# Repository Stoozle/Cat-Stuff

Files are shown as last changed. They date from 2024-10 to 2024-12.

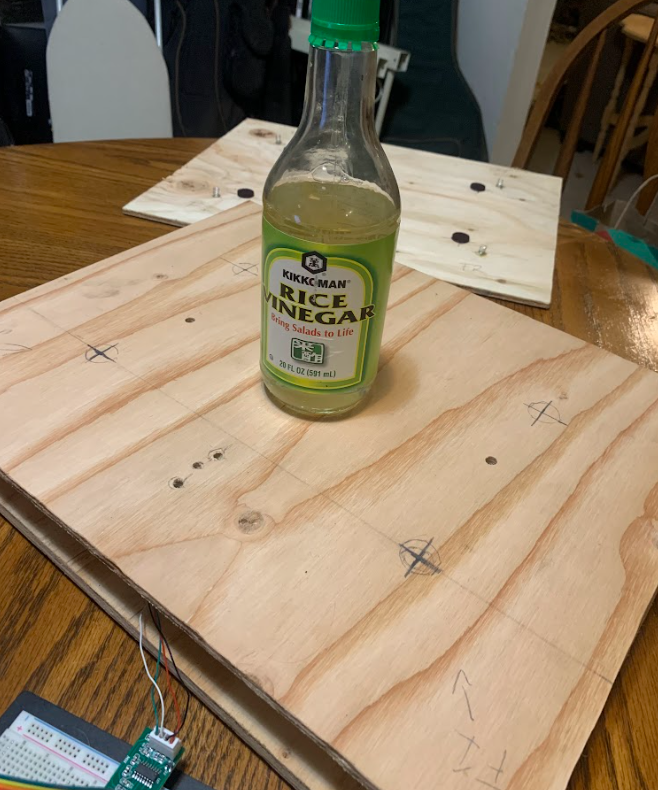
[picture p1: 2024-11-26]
testing/11_15_force_distrubution/center_board.png

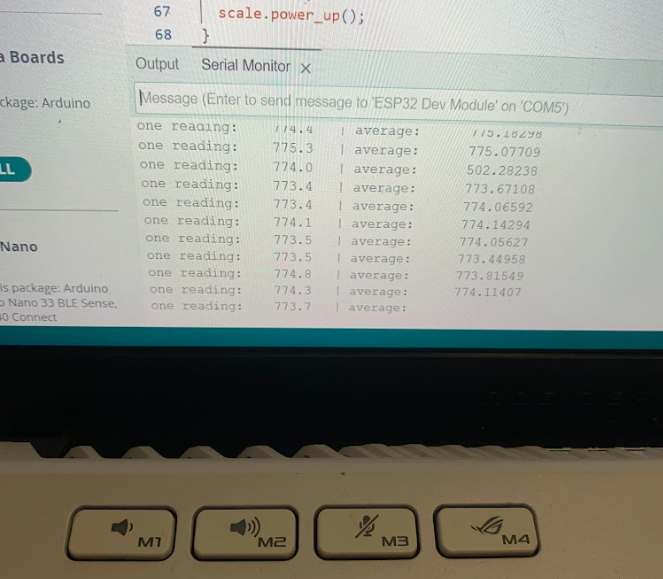
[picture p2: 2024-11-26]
testing/11_15_force_distrubution/left_output.png

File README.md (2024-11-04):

# FLOPS (FeLine Obesity Prevention System)
## High level description (project in development and much is subject to change and refinement)
* Cat owner's may want to monitor their cat's weight for various reasons. This project is intended to provide a system that will automatically measures a cat's weight. Measurement data can be used to inform appropriate modifications to a cat's diet in order to meet a target weight.
## Theory of operation
* Takes a cat's weight measurement every time it sleeps in its bed
* Allows user to observe plot of weight measurements over time

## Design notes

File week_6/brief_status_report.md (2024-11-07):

## Brief status report for team 09

So far we have
* Ordered inital parts/sensors
* Tested flexible force sensors (to detect weight in fixture) to observe output in a simple circuit
* Tested load cell with ADC and acquired weight measurement of a soda can that matches a kitchen scale
* Made progress with communicating with the ESP32 over WiFi
* Narrowed down options for methods of producing the outputs we need to make the scale work, and the types of components we'll need for the peripheral circuitry

We were feeling a little behind but are grinding to catch up and get ahead. The next glut of parts will be in the mail shortly, and more specific testing is soon to follow.

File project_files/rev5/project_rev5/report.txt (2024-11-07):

Info: Processing symbol 'C1:'.
Info: Processing symbol 'U3:'.
Info: Processing symbol 'C2:'.
Info: Processing symbol 'R7:'.
Info: Processing symbol 'C3:'.
Info: Processing symbol 'U1:Package_SO:SOP-16_3.9x9.9mm_P1.27mm'.
Info: Processing symbol 'C4:'.
Info: Processing symbol 'R8:'.
Info: Processing symbol 'J1:'.
Info: Processing symbol 'U2:RF_Module:ESP32-WROOM-32'.
Info: Processing symbol 'J2:'.
Info: Processing symbol 'R9:'.
Info: Processing symbol 'J3:'.
Info: Processing symbol 'X1:Oscillator:Oscillator_DIP-14'.
Info: Processing symbol 'J4:'.
Info: Processing symbol 'R1:'.
Info: Processing symbol 'J5:'.
Info: Processing symbol 'R10:'.
Info: Processing symbol 'J6:'.
Info: Processing symbol 'R2:'.
Info: Processing symbol 'Q1:'.
Info: Processing symbol 'U6:'.
Info: Processing symbol 'Q2:Package_TO_SOT_THT:TO-92_Inline'.
Info: Processing symbol 'R3:'.
Info: Processing symbol 'R11:'.
Info: Processing symbol 'R4:'.
Info: Processing symbol 'U4:'.
Info: Processing symbol 'R5:'.
Info: Processing symbol 'SW1:'.
Info: Processing symbol 'R6:'.
Connected U2 pin 39 to GND.
Connected U2 pin 1 to GND.
Connected U2 pin 39 to GND.
Add net unconnected-(U2-SCK/CLK-Pad20).
Connected U2 pin 20 to unconnected-(U2-SCK/CLK-Pad20).
Added X1 (footprint 'Oscillator:Oscillator_DIP-14').
Changed REF** reference designator to X1.
Changed X1 value from Oscillator_DIP-14 to ACO-11MHz.
Updated X1 symbol association from  to /a301af15-4480-4dae-a242-64f552d5c465.
Updated X1 fields.
Updated X1 sheetname to 'Root'.
Added Q2 (footprint 'Package_TO_SOT_THT:TO-92_Inline').
Changed REF** reference designator to Q2.
Changed Q2 value from TO-92_Inline to S8550.
Updated Q2 symbol association from  to /422a7e9a-33ed-4cef-8547-62cccaa18b52.
Updated Q2 fields.
Updated Q2 sheetname to 'Root'.
Updated Q2 sheetfile to 'project1.kicad_sch'.
Updated Q2 footprint filters to 'TO?92*'.
Add net +3.3V.
Connected Q2 pin 1 to +3.3V.
Add net Net-(Q2-B).
Connected Q2 pin 2 to Net-(Q2-B).
Add net Net-(J2-Pin_1).
Connected Q2 pin 3 to Net-(J2-Pin_1).
Updated X1 sheetfile to 'project1.kicad_sch'.
Updated X1 footprint filters to 'Oscillator*DIP*14*'.
Connected X1 pin 14 to +3.3V.
Connected X1 pin 7 to GND.
Add net unconnected-(X1-OUT-Pad8).
Connected X1 pin 8 to unconnected-(X1-OUT-Pad8).
Add net unconnected-(X1-NC-Pad1).
Connected X1 pin 1 to unconnected-(X1-NC-Pad1).
Added U1 (footprint 'Package_SO:SOP-16_3.9x9.9mm_P1.27mm').
Changed REF** reference designator to U1.
Changed U1 value from SOP-16_3.9x9.9mm_P1.27mm to HX711.
Updated U1 symbol association from  to /569d6c08-9232-4001-98fb-e43093d856b7.
Updated U1 fields.
Updated U1 sheetname to 'Root'.
Updated U1 sheetfile to 'project1.kicad_sch'.
Updated U1 footprint filters to 'SOP*3.9x9.9mm*P1.27mm*'.
Add net GND.
Connected U1 pin 5 to GND.
Connected U1 pin 14 to GND.
Add net unconnected-(U1-XO-Pad13).
Connected U1 pin 13 to unconnected-(U1-XO-Pad13).
Connected U1 pin 15 to GND.
Add net Net-(U1-VBG).
Connected U1 pin 6 to Net-(U1-VBG).
Connected U1 pin 10 to GND.
Connected U1 pin 1 to +3.3V.
Add net Net-(U1-INA-).
Connected U1 pin 7 to Net-(U1-INA-).
Connected U1 pin 9 to GND.
Add net Net-(U1-VFB).
Connected U1 pin 4 to Net-(U1-VFB).
Add net Net-(U1-PD_SCK).
Connected U1 pin 11 to Net-(U1-PD_SCK).
Connected U1 pin 3 to Net-(J2-Pin_1).
Connected U1 pin 16 to +3.3V.
Add net Net-(U1-DOUT).
Connected U1 pin 12 to Net-(U1-DOUT).
Add net Net-(U1-INA+).
Connected U1 pin 8 to Net-(U1-INA+).
Connected U1 pin 2 to Net-(Q2-B).
Added U2 (footprint 'RF_Module:ESP32-WROOM-32').
Changed REF** reference designator to U2.
Updated U2 symbol association from  to /1d41e7d4-28ae-44ed-bed4-c70fb3c3bb19.
Updated U2 fields.
Updated U2 sheetname to 'Root'.
Updated U2 sheetfile to 'project1.kicad_sch'.
Updated U2 footprint filters to 'ESP32?WROOM?32*'.
Add net unconnected-(U2-TXD0/IO1-Pad35).
Connected U2 pin 35 to unconnected-(U2-TXD0/IO1-Pad35).
Connected U2 pin 39 to GND.
Add net unconnected-(U2-EN-Pad3).
Connected U2 pin 3 to unconnected-(U2-EN-Pad3).
Add net unconnected-(U2-NC-Pad32).
Connected U2 pin 32 to unconnected-(U2-NC-Pad32).
Add net unconnected-(U2-IO2-Pad24).
Connected U2 pin 24 to unconnected-(U2-IO2-Pad24).
Add net Net-(Q1-D).
Connected U2 pin 7 to Net-(Q1-D).
Connected U2 pin 27 to Net-(U1-DOUT).
Add net unconnected-(U2-SENSOR_VP-Pad4).
Connected U2 pin 4 to unconnected-(U2-SENSOR_VP-Pad4).
Connected U2 pin 39 to GND.
Connected U2 pin 39 to GND.
Connected U2 pin 15 to GND.
Connected U2 pin 39 to GND.
Add net unconnected-(U2-IO19-Pad31).
Connected U2 pin 31 to unconnected-(U2-IO19-Pad31).
Add net unconnected-(U2-SCS/CMD-Pad19).
Connected U2 pin 19 to unconnected-(U2-SCS/CMD-Pad19).
Connected U2 pin 39 to GND.
Connected U2 pin 39 to GND.
Connected U2 pin 39 to GND.
Add net unconnected-(U2-IO23-Pad37).
Connected U2 pin 37 to unconnected-(U2-IO23-Pad37).
Add net unconnected-(U2-SENSOR_VN-Pad5).
Connected U2 pin 5 to unconnected-(U2-SENSOR_VN-Pad5).
Connected U2 pin 39 to GND.
Add net unconnected-(U2-SDI/SD1-Pad22).
Connected U2 pin 22 to unconnected-(U2-SDI/SD1-Pad22).
Connected U2 pin 39 to GND.
Connected U2 pin 39 to GND.
Connected U2 pin 39 to GND.
Add net unconnected-(U2-IO32-Pad8).
Connected U2 pin 8 to unconnected-(U2-IO32-Pad8).
Connected U2 pin 26 to Net-(U1-PD_SCK).
Add net unconnected-(U2-IO34-Pad6).
Connected U2 pin 6 to unconnected-(U2-IO34-Pad6).
Connected U2 pin 38 to GND.
Add net unconnected-(U2-RXD0/IO3-Pad34).
Connected U2 pin 34 to unconnected-(U2-RXD0/IO3-Pad34).
Connected U2 pin 39 to GND.
Connected U2 pin 39 to GND.
Add net unconnected-(U2-IO27-Pad12).
Connected U2 pin 12 to unconnected-(U2-IO27-Pad12).
Add net unconnected-(U2-SDO/SD0-Pad21).
Connected U2 pin 21 to unconnected-(U2-SDO/SD0-Pad21).
Add net unconnected-(U2-IO26-Pad11).
Connected U2 pin 11 to unconnected-(U2-IO26-Pad11).
Add net unconnected-(U2-IO14-Pad13).
Connected U2 pin 13 to unconnected-(U2-IO14-Pad13).
Add net unconnected-(U2-SHD/SD2-Pad17).
Connected U2 pin 17 to unconnected-(U2-SHD/SD2-Pad17).
Add net unconnected-(U2-IO12-Pad14).
Connected U2 pin 14 to unconnected-(U2-IO12-Pad14).
Connected U2 pin 39 to GND.
Add net unconnected-(U2-IO33-Pad9).
Connected U2 pin 9 to unconnected-(U2-IO33-Pad9).
Connected U2 pin 39 to GND.
Add net unconnected-(U2-IO18-Pad30).
Connected U2 pin 30 to unconnected-(U2-IO18-Pad30).
Add net unconnected-(U2-IO0-Pad25).
Connected U2 pin 25 to unconnected-(U2-IO0-Pad25).
Add net unconnected-(U2-IO15-Pad23).
Connected U2 pin 23 to unconnected-(U2-IO15-Pad23).
Connected U2 pin 39 to GND.
Add net unconnected-(U2-IO22-Pad36).
Connected U2 pin 36 to unconnected-(U2-IO22-Pad36).
Connected U2 pin 39 to GND.
Connected U2 pin 39 to GND.
Add net unconnected-(U2-IO25-Pad10).
Connected U2 pin 10 to unconnected-(U2-IO25-Pad10).
Add net unconnected-(U2-SWP/SD3-Pad18).
Connected U2 pin 18 to unconnected-(U2-SWP/SD3-Pad18).
Connected U2 pin 39 to GND.
Connected U2 pin 39 to GND.
Connected U2 pin 2 to +3.3V.
Add net unconnected-(U2-IO17-Pad28).
Connected U2 pin 28 to unconnected-(U2-IO17-Pad28).
Add net unconnected-(U2-IO21-Pad33).
Connected U2 pin 33 to unconnected-(U2-IO21-Pad33).
Add net unconnected-(U2-IO13-Pad16).
Connected U2 pin 16 to unconnected-(U2-IO13-Pad16).
Add net unconnected-(U2-IO5-Pad29).
Connected U2 pin 29 to unconnected-(U2-IO5-Pad29).
Error: Cannot add C1 (no footprint assigned).
Error: Cannot add C2 (no footprint assigned).
Error: Cannot add C3 (no footprint assigned).
Error: Cannot add C4 (no footprint assigned).
Error: Cannot add J1 (no footprint assigned).
Error: Cannot add J2 (no footprint assigned).
Error: Cannot add J3 (no footprint assigned).
Error: Cannot add J4 (no footprint assigned).
Error: Cannot add J5 (no footprint assigned).
Error: Cannot add J6 (no footprint assigned).
Error: Cannot add Q1 (no footprint assigned).
Error: Cannot add R1 (no footprint assigned).
Error: Cannot add R2 (no footprint assigned).
Error: Cannot add R3 (no footprint assigned).
Error: Cannot add R4 (no footprint assigned).
Error: Cannot add R5 (no footprint assigned).
Error: Cannot add R6 (no footprint assigned).
Error: Cannot add R7 (no footprint assigned).
Error: Cannot add R8 (no footprint assigned).
Error: Cannot add SW1 (no footprint assigned).
Error: Cannot add U3 (no footprint assigned).
Error: Cannot add R11 (no footprint assigned).
Error: Cannot add U4 (no footprint assigned).
Error: Cannot add R10 (no footprint assigned).
Error: Cannot add U6 (no footprint assigned).
Error: Cannot add R9 (no footprint assigned).

Info: Total warnings: 0, errors: 26.

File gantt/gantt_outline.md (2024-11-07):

Working out dependencies

# Physical structure/enclosure

## PCBA Enclosure
    • 3D CAD tutorial/learn basics
    • Make a box in CAD (something simple, but on your own) and printable
    • 3D print the box, for experience in the process
    • Make it more complex - add in spaces for wires to exit, mounting holes, a top that can be screwed on, etc. 
    NOTE: At this point is just needs to have the elements we need for an enclosure, but good enough that once we have our boards

## Bed Structure
    • Brainstorm material types, general requirements, sizing
    • Sketch out structure, all major components
    • Make prototype out of basic cheap material - cardboard or foam board is fine
    • Collect materials - go to hardware store to see what's available, buy

## Display of measurements
    • Research ways to display plot of data to user
    • Test methods of visual data representation
        ○ Screen mounted to bed housing
            • Research libraries for interpretation of user input
            • Implement interface for user input
            • Test if user input (WiFi name) is handled correctly
        ○ Web browser
            • Determine how it will receive information
            • Code interpretation of data received
            • Code data storage scheme
            • Code user output

## Wireless Communication
    • Research methods to transmit data wirelessly from ESP32
    • Test methods (contingent upon selection of web browser, mobile app - Wifi or bluetooth, or combination)
        ○ WiFi 
            • Research how to do http post on ESP32 using either wifi.h or httpclient.h arduino libraries
            • Setup client server scheme on ESP32
            • Test communication with outside server

## Load Cell/Strain Gauge - Sensor 
    • Research types of sensors that can be used for measuring weight
    • Get load cell and ADC, additional components ala datasheet
    • Get force reading from strain gauge and ADC on breakout board and ESP32 dev board
    • Transmit and receive force reading wirelessly 

## Force Sensor Circuit
    • Research force sensors
    • Select force sensors
    • Design force sensor circuit
    • Order force sense circuit parts
    • Test sensitivity with weights according to data sheet
    • Test if ESP32 responds to interpretation logic
    
## Power
    • Research what's required for power needs
    • Design power distribution circuit
    • Order parts
* Test circuit

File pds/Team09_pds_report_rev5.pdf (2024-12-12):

Version | Date
V 1 | 10/23/24
V 2 | 10/31/24
V3 | 11/20/24
V4 | 12/5/24
V5 | 12/10/24

## Product Design Specification

## Team 9: FLOPS

Authors:
Tim Hoke
Mohammad Alshaiji
Luis Hilbert Rivas
Stuart Packard

Course:
ECE 411
Introduction to Industry Design Fall 2024
PDS sheet

### Product Name

The name of the product is “The FLOPS”! Which stands for the FeLine Obesity Prevention System.

### Executive Summary with Concept of Operations

The device helps cat owners achieve their cat’s target weight by automatically recording weight measurements. Each time the cat enters its bed, the device records a weight measurement and stores the result. Users can log the amount of food they give their cat, and based on their target weight, adjust the feeding amounts to see how it affects the cat’s weight. The software’s user interface displays these weight trends in easy-to-read plots, allowing users to observe and track trends over time. They can use the trends to make an informed decision on how to adjust their cat's diet.

This approach is valuable for managing a cat’s weight, whether the goal is to address overweight, underweight, or maintain optimal health. Unlike relying solely on observation, the device offers a precise, data-driven method for weight management. It automates data collection, minimizing the need for manual effort from the owner.

Although regular vet visits remain essential, this device provides insight into weight changes between those visits, which typically occur only once or twice a year.

### Brief Market Analysis

Cat owners who need to manage their cat’s weight will benefit from this product, especially those who struggle to weigh their cat. Some cats, being timid, won’t let their owners pick them up and place them on a scale. In some cases, owners have physical impairments that make it difficult or impossible to lift their pet. Our product provides a solution by automatically weighing the cat in its bed. It also appeals to gadget lovers who enjoy the convenience of automated tools. Although designed for cats, small dog owners can also use this scale, and we plan to expand to larger pets in the future.

Our main competitors include brands that sell at pet supply retailers like Petco, PetSmart, and of course, Amazon. Companies such as IBE Supply and Unipaws focus on offering scales with digital readouts and comfortable seating for pets. Some of these companies, like Unipaws, also let users track measurements through a Bluetooth connection to a smartphone.

Our design stands out from other pet scales. We’ve created a form factor that integrates with a cat bed, using curved or beveled edges to hold it securely in place. Unlike competitors’ steel-plate scales, our product offers a more attractive, cat-bed-like aesthetic. More importantly, the scale provides automatic and continuous weight measurements, so users don’t need to forcibly weigh their pets. This allows owners to monitor weight fluctuations more frequently.

Competitor products range from $60 for basic designs to $125-$150 for those with digital readouts and Bluetooth features. Our components cost around $50, so we can sell this product for $99.99, offering more features at a lower price than the competition, while still maintaining a healthy profit margin.

### Requirements

- Must have continuous power; the system needs to be online and ready to take a measurement whenever a cat lays on its bed.
- Must be able to collect data points of weight over time and display a plot of data to the user.
- Must collect data automatically.
- Must not have to manually put the cat onto the scale in order to get weight measurements.
- Must be able to handle the weight of a cat for an extended period of time.
- Must be able to accurately measure within the normal weight range of a cat.
- Must be sensitive enough for the force sensors to accurately determine that the cat is in the bed.
- Should have an indication that power is on for the user.
- Should be able to display force as a function of time graph to users quickly.
- Should display graphs and tables of previous values from a website or other application.
- May have something interesting like a toy for the cat to interact with.
- May have an interface for the user to input internet access credentials.

### System Architecture

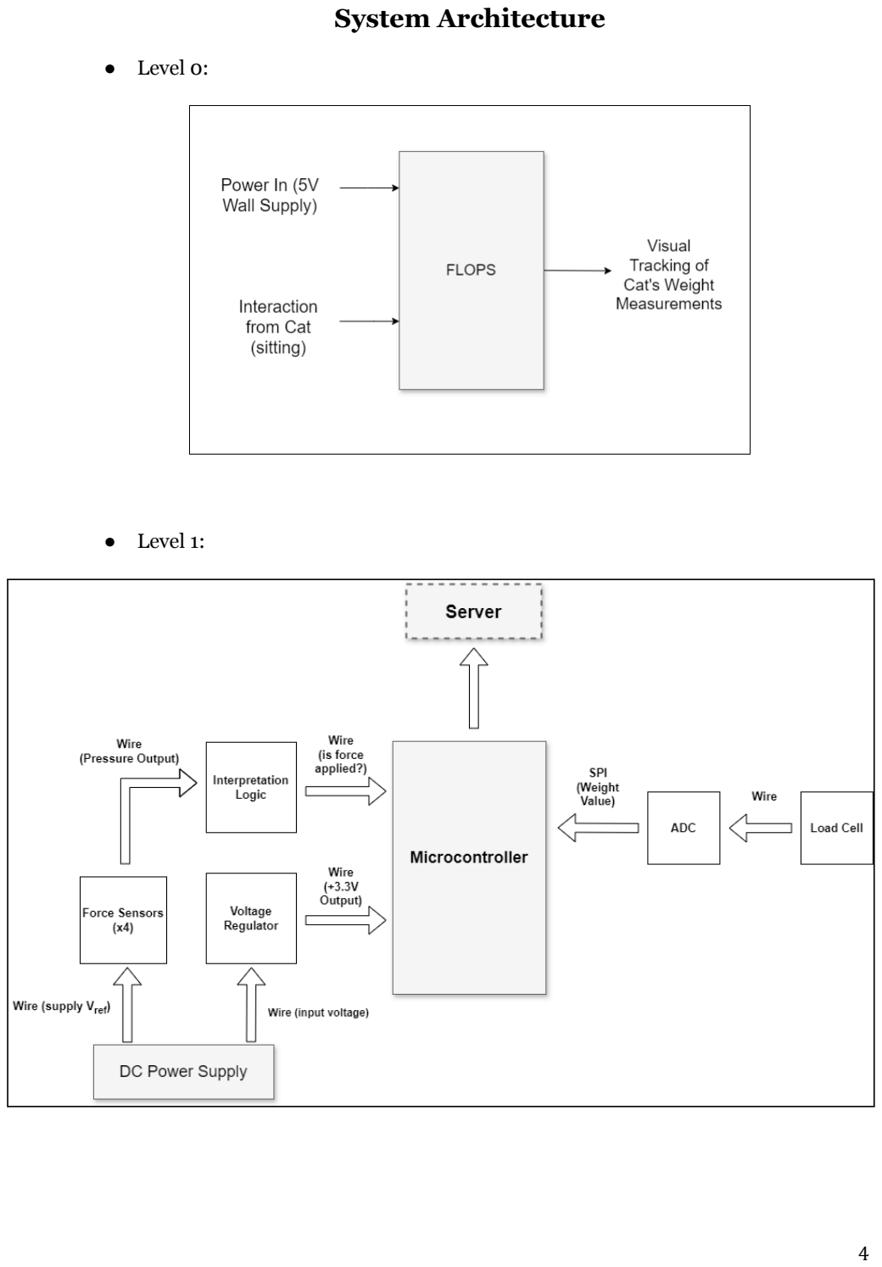
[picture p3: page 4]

- Level 0:
- Level 1:

### Design Specification

- 5V wall plug for power supply:
■ Plugged into the barrel jack on the housing.
■ Voltage regulator IC’s for powered components that aren’t 5V tolerant.
- Strain Gauges:
■ Metallic foil strain gauge for weight measurement.
■ Mounted to stiff lower platforms.
■ Adafruit Strain Gauge Load Cell - 20kg max
- ADC :
■ High Precision reading output for strain gauge communication. ■ SPI output.
■ Avia Semiconductor HX711 - 24 bit ADC IC
- ESP32:
■ Signal and data processing controller.
■ Espressif ESP32 S3-WROOM S3-1-N16R8 - rx/tx Bluetooth & WiFi module
- Mechanical Aspects:
■ Square surface of cat bed, pressure sensors on underside of surface
■ Enclosure for Load Cell and PCBA.
- Flexible Piezoresistive Pressure Sensors.
■ For detecting pressure from a cat sitting in bed.
■ 4 sensors feed into 4 input, single output AND gate.
■ Output of AND gate to gate to power MOSFET to allow power on for ESP32, ADC/strain gauge.
■ Uneo Tech GHF10 - 0-500N max
- Data Display
■ Web server to offload data from the ESP32 over WiFi for storage and user interaction.
■ Touch screen for user to enter WiFi credentials
■ Expressif IDF and Platform.io have VSCode extensions popular for ESP32 programming, as does the Arduino IDE.

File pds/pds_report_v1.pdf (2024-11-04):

Team 9
Tim Hoke
Mohammad Alshaiji
Luis Hilbert Rivas
Stuart Packard
ECE 411 - Fall 2024
PDS design sheet
Due: 10/24/24
Rev1

## Product Design Specification

- Product Name
- The FOPS! Feline Obesity Prevention System.
- Executive Summary with Concept of Operations

The device helps cat owners achieve their cat’s target weight by automatically recording weight measurements. Each time the cat enters its bed, the device records a weight measurement and stores the result. Users can log the amount of food they give their cat, and based on their target weight, adjust the feeding amounts to see how it affects the cat’s weight. The software’s user interface displays these weight trends in easy-to-read plots, allowing users to observe and track trends over time. They can use the trends to make an informed decision on how to adjust their cat's diet.

This approach is valuable for managing a cat’s weight, whether the goal is to address overweight, underweight, or maintain optimal health. Unlike relying solely on observation, the device offers a precise, data-driven method for weight management. It automates data collection, minimizing the need for manual effort from the owner.

Although regular vet visits remain essential, this device provides insight into weight changes between those visits, which typically occur only once or twice a year.

- Brief “Market” Analysis

Cat owners who need to manage their cat’s weight will benefit from this product, especially those who struggle to weigh their cat. Some cats, being timid, won’t let their owners pick them up and place them on a scale. In some cases, owners have physical impairments that make it difficult or impossible to lift their pet. Our product provides a solution by automatically weighing the cat in its bed. It also appeals to gadget lovers who enjoy the convenience of automated tools. Although designed for cats, small dog owners can also use this scale, and we plan to expand to larger pets in the future.

Our main competitors include brands that sell at pet supply retailers like Petco, PetSmart, and of course, Amazon. Companies such as IBE Supply and Unipaws focus on offering scales with digital readouts and comfortable seating for pets. Some of these companies, like Unipaws, also let users track measurements through a Bluetooth connection to a smartphone.

Our design stands out from other pet scales. We’ve created a form factor that integrates with a cat bed, using curved or beveled edges to hold it securely in place. Unlike competitors’ steel-plate scales, our product offers a more attractive, cat-bed-like aesthetic. More importantly, the scale provides automatic and continuous weight measurements, so users don’t need to forcibly weigh their pets. This allows owners to monitor weight fluctuations more frequently.

Competitor products range from $60 for basic designs to $125-$150 for those with digital readouts and Bluetooth features. Our components cost around $50, so we can sell this product for $99.99, offering more features at a lower price than the competition, while still maintaining a healthy profit margin.

- Requirements
- Must have continuous power; the system needs to be online and ready to take a measurement whenever a cat lays on its bed.
- Must be able to collect data points of weight over time and display a plot of data to the user.
- Must collect data automatically.
- Users must not have to manually put the cat onto the scale in order to get weight measurements.
- Must be able to weigh a cat accurately within the normal weight range of a cat.
- Must be able to communicate with a custom software application to observe collected data.
- Should be able to zero out scale manually with display or interface on the device.
- Should have an indication that power is on.
- Should have something interesting for the cat to interact with.
- Should be shaped in a way that encourages long term sitting by the cat.
- Should be able to display force as function of time graph to user quickly.
- Website/application should display graphs and tables of previous values.

System Architecture

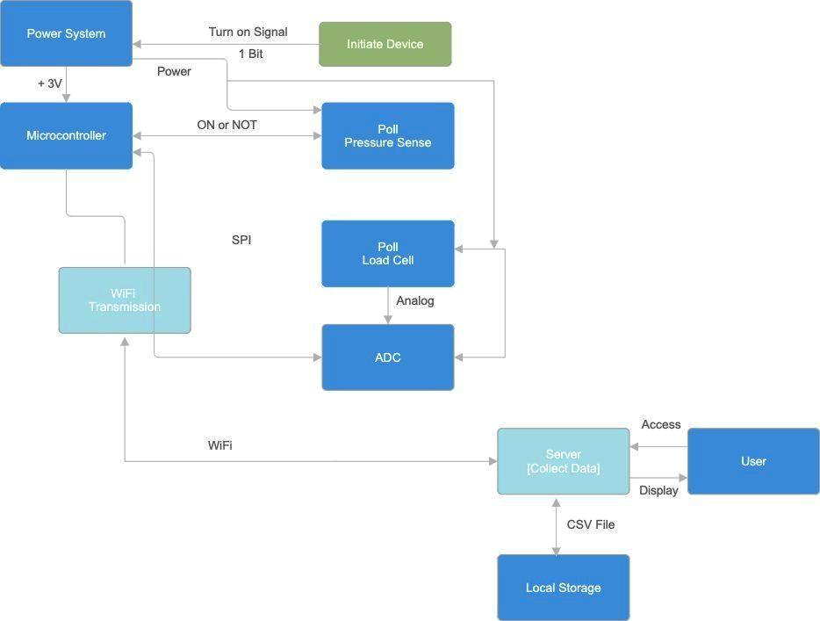
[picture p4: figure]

- Level 0:

- Level 1:

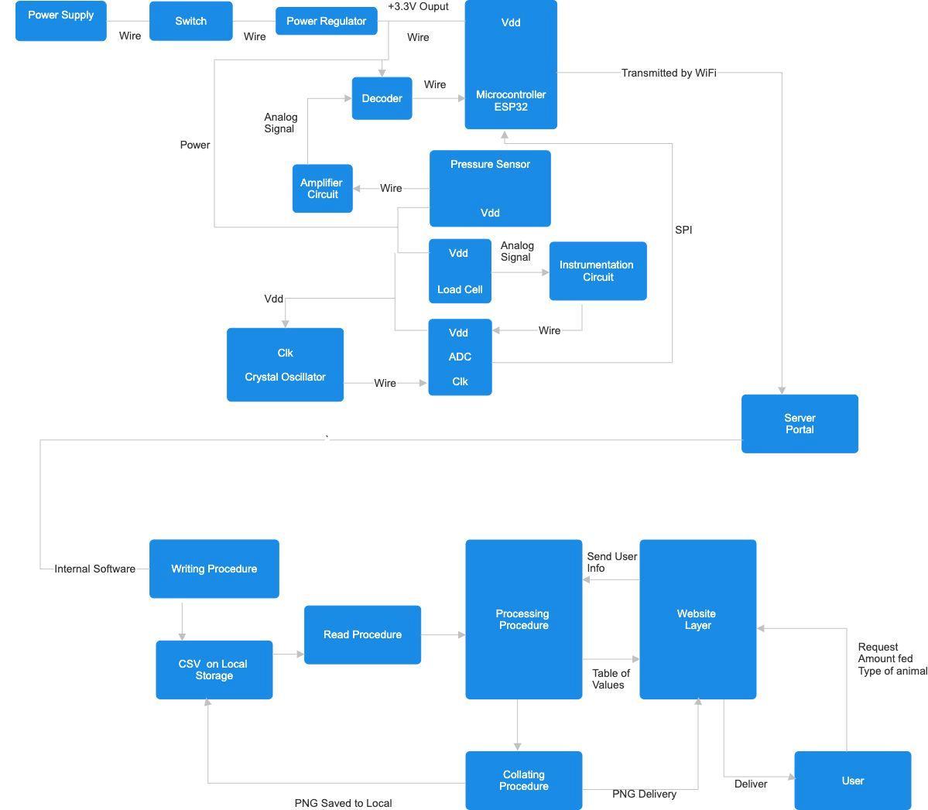
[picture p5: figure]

- Design Specification
- 5V wall plug for power supply, plugged into barrel jack on housing. Voltage regulator ICs for powered components that aren’t 5V tolerant.
- Metallic foil strain gauge for weight measurement
- High precision ADC for reading output of strain gauge, SPI output
- ESP32 will be the controller that accepts and processes signals/data
- Strain gauge will be mounted to stiff upper and lower platform
- The mechanical portion will be a rectangular surface and enclosure for load cell and PCBA.
- Flexible piezoresistive polymer composite pressure sensors serve as actuator. * * Pressure on sensor will indicate to the controller to take measurement.
- A web server will be set up to offload data from the ESP32 over WiFi for storage and user interaction.
- Espressif IDF and Platform.io have VSCode extensions popular for ESP32 programming. So is Arduino IDE.

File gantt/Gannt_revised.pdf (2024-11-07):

Gannt_revised | Nov 7, 2024 http://

Project manager
Project dates | Oct 10, 2024 - Dec 14, 2024
Completion | 43%
Tasks | 52
Resources | 4

Name | Begin date | End date
Design PCBA Enclosure | 10/28/24 | 10/28/24
Learn Basics of 3d CAD | 10/29/24 | 10/30/24
Make a box in CAD | 10/31/24 | 11/1/24
Print 3d model of box | 11/4/24 | 11/8/24
Alter Design to Increased Complexity | 11/11/24 | 11/13/24
Design/Implement Bed Structure | 10/31/24 | 10/31/24
BrainStorm Materials | 11/1/24 | 11/1/24
Sketch Out Structure and Components | 11/4/24 | 11/8/24
Create Initial Prototype | 11/11/24 | 11/13/24
Iterate on protoype and Create Final Design | 11/14/24 | 11/19/24
Work on Display of Measurements | 10/18/24 | 10/18/24
Research ways to display plot of data to user | 10/21/24 | 10/22/24
Test methods of visual data representation | 10/23/24 | 10/24/24
Screen mounted to bed housing | 10/28/24 | 10/28/24
Research libraries for interpretation of user input | 10/29/24 | 10/30/24
Implement interface for user input | 10/31/24 | 11/1/24
Test if user input (WiFi name) is handled correctly | 11/4/24 | 11/8/24
Web browser | 11/12/24 | 11/12/24
Determine how it will receive information | 11/13/24 | 11/13/24
Code interpretation of recieved data | 11/14/24 | 11/15/24
Code data storage scheme | 11/14/24 | 11/15/24
Implement Display of Output for Users | 11/18/24 | 11/20/24
Wireless Communication | 10/28/24 | 10/28/24
Research methods to transmit data wirelessly from ESP32 | 10/29/24 | 10/30/24
Research how to do http post on ESP32 using either wifi.h or httpclient.h arduino libraries | 10/31/24 | 11/1/24
Setup client server scheme on ESP32 | 11/4/24 | 11/5/24
Test communication with outside server | 11/6/24 | 11/11/24
Gannt_revised | Nov 7, 2024
Tasks | 2

Name | Begin date | End date
Load Cell/Strain Gauge - Sensor | 10/28/24 | 10/28/24
Research types of sensors that can be used for measuring weight | 10/29/24 | 10/30/24
Get load cell and ADC, additional components ala datasheet | 10/31/24 | 11/5/24
Get force reading from strain gauge and ADC on breakout board and ESP32 dev board | 10/31/24 | 11/4/24
Transmit and receive force reading wirelessly | 11/6/24 | 11/11/24
Force Sensor Circuit | 10/28/24 | 10/30/24
Research force sensors | 11/6/24 | 11/6/24
Select force sensors | 11/7/24 | 11/8/24
Design force sensor circuit | 11/11/24 | 11/14/24
Order force sense circuit parts | 11/7/24 | 11/13/24
Test sensitivity with weights according to data sheet | 11/15/24 | 11/19/24
Test if ESP32 responds to interpretation logic | 11/15/24 | 11/19/24
Power Circuit | 10/28/24 | 10/28/24
Research what's required for power needs | 11/4/24 | 11/5/24
Design power distribution circuit | 11/6/24 | 11/8/24
Order parts for Power Circuit | 11/6/24 | 11/11/24
Implement Power Circuit | 11/12/24 | 11/14/24
Test Power Circuit | 11/15/24 | 11/15/24
Finalize Research | 11/11/24 | 11/11/24
Integrate Hardware Circuitry | 11/21/24 | 11/27/24
Integrate Hardware and Software | 11/28/24 | 12/3/24
Finalize Integration | 12/4/24 | 12/6/24
TESTING!!!! | 12/9/24 | 12/13/24
Generate Three Project Ideas | 10/10/24 | 10/17/24
Work on PDS | 10/18/24 | 10/25/24
Tasks | 3

Name | Default role
Liuz H | undefined
Mohammad A | undefined
Tim H | undefined
Stuart P | undefined
Resources | 4

## Gantt Chart

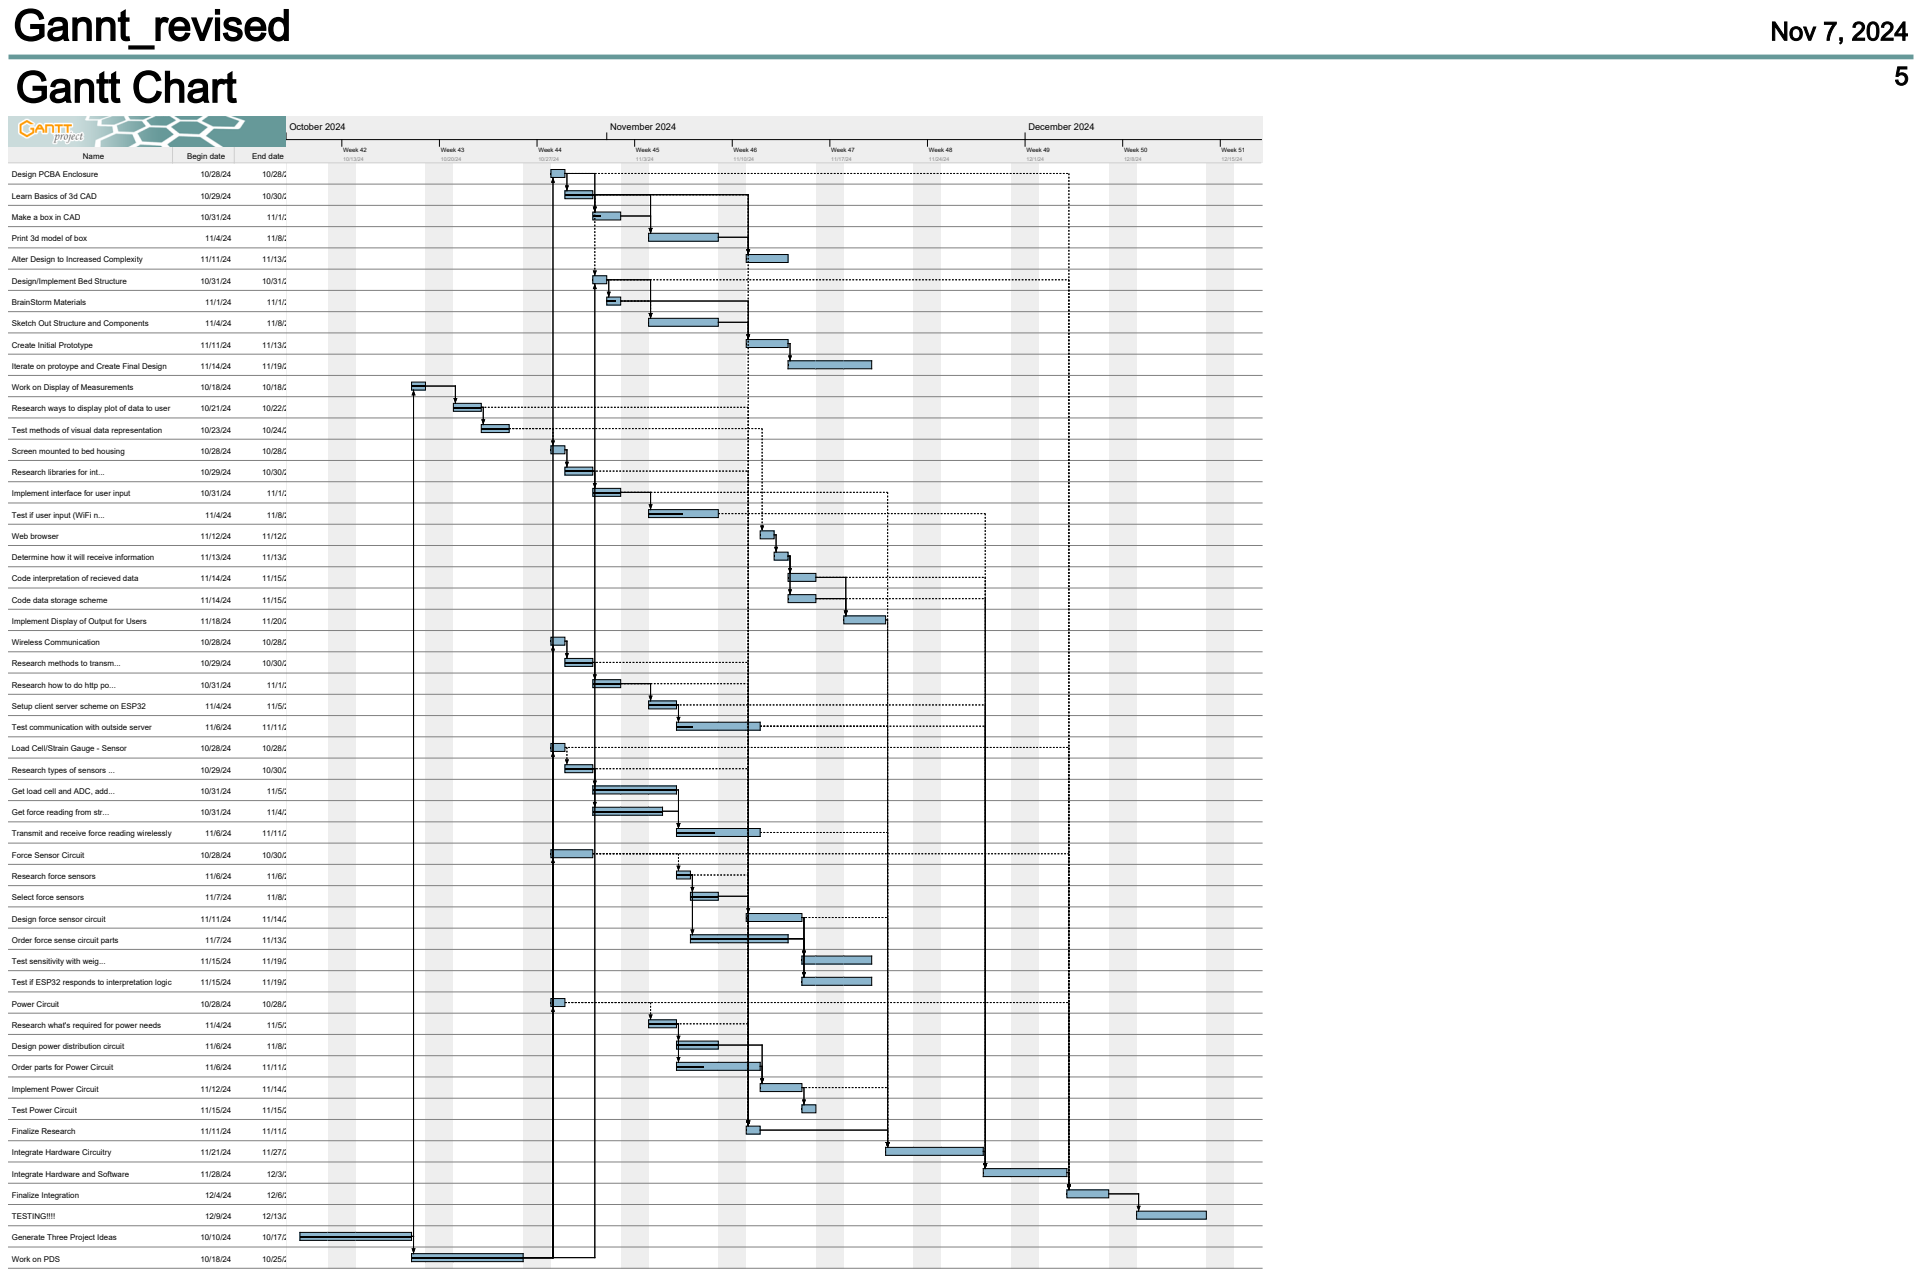
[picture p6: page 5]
Name; Begin date; End date; Design PCBA Enclosure; Learn Basics of 3d CAD; Make a box in CAD; Print 3d model of box; Alter Design to Increased Complexity; Design/Implement Bed Structure; BrainStorm Materials; Sketch Out Structure and Components; Create Initial Prototype; Iterate on protoype and Create Final Design; Work on Display of Measurements; Research ways to display plot of data to user; Test methods of visual data representation; Screen mounted to bed housing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

## Resources Chart

6

Name | Default role
Liuz H | undefined

Print 3d model of box

Alter Design to Increase...

BrainStorm Materials

Create Initial Prototype

Iterate on protoype and ...

Determine how it will rec...

Implement Display of Ou...

Transmit and receive for...

Order force sense circuit...

Test sensitivity with weig...

Research what's require...

Order parts for Power Ci...

Implement Power Circuit

Finalize Research

Integrate Hardware Circ...

Finalize Integration

TESTING!!!!

Generate Three Project I...

Work on PDS

Mohammad A | undefined

Work on Display of Mea...

Research ways to displa...

Test methods of visual d...

Design/Implement Bed ...

BrainStorm Materials

Research libraries for int...

Implement interface for ...

Test if user input (WiFi n...

Determine how it will rec...

Code interpretation of re...

Code data storage sche...

Research methods to tra...

Research how to do http...

Setup client server sche...

Test communication wit...

Transmit and receive for...

Design force sensor circuit

Test if ESP32 responds t...

Order parts for Power Ci...

Test Power Circuit

Finalize Research

Integrate Hardware and ...

Finalize Integration

TESTING!!!!

Generate Three Project I...

Work on PDS

Tim H | undefined

Design PCBA Enclosure

Learn Basics of 3d CAD

Make a box in CAD

Print 3d model of box

Alter Design to Increase...

Iterate on protoype and ...

Implement Display of Ou...

Research types of sens...

Research force sensors

Design force sensor circuit | 20%

Order force sense circuit...

Test sensitivity with weig...

Research what's require...

Design power distributio...

Order parts for Power Ci...

Implement Power Circuit

Finalize Research

Integrate Hardware Circ...

Finalize Integration

TESTING!!!!

Generate Three Project I...

Work on PDS

Stuart P | undefined

Test methods of visual d...

Load Cell/Strain Gauge ...

Design/Implement Bed ...

BrainStorm Materials

Sketch Out Structure an...

Create Initial Prototype

Get load cell and ADC, ...

Get force reading from st...

Transmit and receive for...

Research force sensors

Select force sensors

Design force sensor circuit

Order force sense circuit...

Test if ESP32 responds t...

Design power distributio...

Order parts for Power Ci...

Implement Power Circuit

Test Power Circuit

Finalize Research

Integrate Hardware and ...

Finalize Integration

TESTING!!!!

Generate Three Project I...

Work on PDS

30% | 200% | 400% | 300%

30%

20%

200% | 200% | 200% | 200% | 400%

30%

30%

200% | 200% | 400% | 320% | 300%
200% | 600% | 400%
October 2024 | November 2024 | December 2024
Week 41 | Week 42 | Week 43 | Week 44 | Week 45 | Week 46 | Week 47 | Week 48 | Week 49 | Week 50 | Week 51
10/6/24 | 10/13/24 | 10/20/24 | 10/27/24 | 11/3/24 | 11/10/24 | 11/17/24 | 11/24/24 | 12/1/24 | 12/8/24 | 12/15/24

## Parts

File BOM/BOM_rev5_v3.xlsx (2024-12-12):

Bill Of Material for: | Team Number 9
Last modified: | 2024-12-06
PCB version: | PCB Version #5
BOM revision: | BOM revision # 3
Quantity | Part References | P/NP | Mfg | Mfg PN | Description | Dist | Dist Part Number | Cost Ea. | Cost Total
1 | U2 | P | Texas Instrument | SN74LS21DR | IC GATE AND 2CH 4-INP 14SOIC | Digi Key | 296-38800-1-ND | $0.63 | $0.63
1 | Q1 | P | Infineon Technologies | BSS816NWH6327XTSA1 | MOSFET N-CH 20V 1.4A SOT323-3 | Digi Key | BSS816NWH6327XTSA1CT-ND | $0.31 | $0.31
1 | U4 | P | Microchip Technology | MCP6004T-I/SL | IC OPAMP GP 4 CIRCUIT 14SOIC | Digi Key | MCP6004T-I/SLCT-ND - Cut Tape (CT) | $0.54 | $0.54
1 | U5 | P | Espressif Systems | ESP32-S3-WROOM-1-N16R8 | RF TXRX MOD BT WIFI PCB TH SMD | Digi Key | 1965-ESP32-S3-WROOM-1-N16R8CT-ND | $3.90 | $3.90
1 | J8 | P | Amphenol ICC (FCI) | 10155435-00011LF | USB TYPE C R/A SMT 16PIN | Digi Key | 609-10155435-00011LFCT-ND | $1.04 | $1.04
1 | D1 | P | Diodes Incorporated | 1N5819HW-7-F | DIODE SCHOTTKY 40V 1A SOD123 | Digi Key | 1N5819HW-FDICT-ND | $0.25 | $0.25
2 | S1, S2 | P | C&K | PTS810SJM250SMTR LFS | SWITCH TACTILE SPST-NO 0.05A 16V | Digi Key | CKN10502CT-ND | $0.58 | $1.16
2 | U3, U6 | P | UMW | AMS1117-3.3 | IC LDO REG 3.3V 1A SOT223 | Digi Key | 4518-AMS1117-3.3CT-ND | $0.39 | $0.78
3 | D2, D3, D4 | P | MDD | ESD5B5CU | TVS DIODE 5VWM 10.5VC SOD523 | Digi Key | 3372-ESD5B5CUTR-ND | $0.12 | $0.36
2 |  | NP | Lumex Opto/Components Inc. | SML-LXFT0603GC-TR | LED GREEN CLEAR SMD | Digi Key | 67-SML-LXFT0603GC-TRCT-ND | $0.39 | $0.78
4 | RV1, RV2, RV3, RV4 | P | Bourns Incorporated | 3314G-1-104E | TRIMMER 100K OHM 0.25W GW TOP | Digi Key | 3314G-104ECT-ND | $1.94 | $7.76
1 | SW1 | P | C & K | JS102011SAQN | SWITCH SLIDE SPDT 300MA 6V | Digi Key | 401-1999-1-ND | $0.84 | $0.84
1 | Q2 | P | Shenzhen Slkormicro Semicon Co., Ltd. | S8550 | 25V 300MW 0.5A PNP SOT-23 BJT | Digi Key | 5399-S8550CT-ND | $0.10 | $0.10
5 | J3,J4,J5,J6,J7 | P | JST Sales America Inc. | S02B-PASK-2 | CONN HEADER R/A 2POS 2MM | Digi Key | 455-S02B-PASK-2-ND | $0.36 | $1.80
4 |  | NP | JST Sales America Inc. | PAP-02V-S | CONN RCPT HSG 2POS 2.00MM | Digi Key | 455-1486-ND | $0.15 | $0.60
1 | J2 | P | JST Sales America Inc. | S04B-PASK-2 | CONN HEADER R/A 4POS 2MM | Digi Key | 455-S04B-PASK-2-ND | $0.41 | $0.41
1 |  | NP | JST Sales America Inc. | PAP-04V-S | CONN RCPT HSG 4POS 2.00MM | Digi Key | 455-1488-ND | $0.17 | $0.17
7 | C1, C5,C7 ,C9 ,C13 ,C15 ,C17 | P | Samsung Electro-Mechanics | CL10A106MQ8NNNC | CAP CER 10UF 6.3V X5R 0603 | Digi Key | 1276-1119-1-ND | $0.10 | $0.70
10 | C2,C3,C4,C6,C8,C10,C11,C14,C16,C18 | P | YAGEO | CC0603KRX7R7BB104 | CAP CER 0.1UF 16V X7R 0603 | Digi Key | 311-1088-1-ND | $0.10 | $1.00
1 | C12 | P | Samsung Electro-Mechanics | CL10B105KP8NNNC | CAP CER 1UF 10V X7R 0603 | Digi Key | 1276-1946-1-ND | $0.10 | $0.10
1 | J1 | P | Same Sky (Formerly CUI Devices) | PJ-002B | CONN PWR JACK 2.5X5.5MM SOLDER | Digi Key | CP-002B-ND | $0.66 | $0.66
1 | U1 | P | Avia Semicon (Xiamen) | HX711 | TREO 24-BIT LOAD CELL ADC 24 2.6V~5.5V SOP-16 Analog to Digital Converters (ADC) ROHS | lcsc | C43656 | $0.45 | $0.45
3 | R1, R6, R7 | P | Panasonic Electronic Components | ERJ-3EKF1000V | RES SMD 100 OHM 1% 1/10W 0603 | Digi Key | P100HCT-ND | $0.10 | $0.30
2 | R2, R12 | P | Panasonic Electronic Components | ERA-3ARW512V | RES SMD 5.1KOHM 0.05% 1/10W 0603 | Digi Key | P5.1KBECT-ND | $0.68 | $1.36
4 | R3, R13, R14, R15 | P | YAGEO | RC0603FR-0710KL | RES 10K OHM 1% 1/10W 0603 | Digi Key | 311-10.0KHRCT-ND | $0.10 | $0.40
1 | R4 | P | Panasonic Electronic Components | ERJ-3EKF2002V | RES SMD 20K OHM 1% 1/10W 0603 | Digi Key | P20.0KHCT-ND | $0.10 | $0.10
1 | R5 | P | Panasonic Electronic Components | ERJ-3EKF8201V | RES SMD 8.2K OHM 1% 1/10W 0603 | Digi Key | P8.20KHCT-ND | $0.10 | $0.10
2 | D5, D8 | P | Würth Elektronik | 150060BS75000 | LED BLUE CLEAR 0603 SMD | Digikey | 732-4966-6-ND | $0.15 | $0.30
1 | D6 | P | Würth Elektronik | 150060GS75000 | LED GREEN CLEAR 0603 SMD |  |  | $0.15 | $0.15
1 | D7 | P | Würth Elektronik | 150060RS75000 | LED RED CLEAR 0603 SMD | Digikey | 732-4978-1-ND | $0.15 | $0.15
1 | Force Sensors 4 Pack | NP | Ezweiji | Generic | 10mm Dia Touch / Pressure Sensor | Digikey | 3917-GD-10-ND | $12.99 | $12.99
1 | Load Cell | NP | Adafruit | 4542 | STRAIN GAUGE LOAD CELL - 4 WIRES | Digikey | 1528-4542-ND | $3.95 | $3.95
 |  |  |  |  |  |  |  | Unit Cost | $44.14
Rev | Date |  | Notes
rev_0 | 2024-11-10 |  | Initial BOM
rev_1 | 2024-11-13 |  | BOM official for rough draft of board
rev_2 | 2024-11-19 |  | final BOM rev_5

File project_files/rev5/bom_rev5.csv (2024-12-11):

Reference | Value | Datasheet | Footprint | Qty | DNP
C1,C5,C7,C9,C13,C15,C17 | 10uF | ~ | Capacitor_SMD:C_0603_1608Metric_Pad1.08x0.95mm_HandSolder | 7
C2,C3,C4,C6,C8,C10,C11,C14,C16,C18 | 0.1uF | ~ | Capacitor_SMD:C_0603_1608Metric_Pad1.08x0.95mm_HandSolder | 10
C12 | 1uf | ~ | Capacitor_SMD:C_0603_1608Metric_Pad1.08x0.95mm_HandSolder | 1
D1 | 1N5819-HW-7-F | http://www.vishay.com/docs/88525/1n5817.pdf | Diode_SMD:D_SOD-123 | 1
D2,D3,D4 | ESD9B5.0ST5G | https://www.onsemi.com/pub/Collateral/ESD9B-D.PDF | Diode_SMD:D_SOD-923 | 3
D5,D6,D8 | 150060BS75000 | ~ | LED_SMD:LED_0603_1608Metric | 3
D7 | 150060RS75000 | ~ | LED_SMD:LED_0603_1608Metric | 1
J1 | Barrel_Jack | ~ | Connector_BarrelJack:BarrelJack_Kycon_KLDX-0202-xC_Horizontal | 1
J2 | Conn_01x04 | ~ | Connector_JST:JST_XA_S04B-XASK-1N-BN_1x04_P2.50mm_Horizontal | 1
J3,J4,J5,J6,J7 | Conn_01x02 | ~ | Connector_JST:JST_XA_S02B-XASK-1N-BN_1x02_P2.50mm_Horizontal | 5
J8 | USB_C_Receptacle_USB2.0_16P | https://www.usb.org/sites/default/files/documents/usb_type-c.zip | Connector_USB:USB_C_Receptacle_GCT_USB4105-xx-A_16P_TopMnt_Horizontal | 1
J10 | Conn_01x09 | ~ | Connector_PinHeader_2.54mm:PinHeader_1x09_P2.54mm_Vertical | 1
J11 | Conn_01x10 | ~ | Connector_PinHeader_2.54mm:PinHeader_1x10_P2.54mm_Vertical | 1
J12 | Conn_01x12 | ~ | Connector_PinHeader_2.54mm:PinHeader_1x12_P2.54mm_Vertical | 1
Q1 | BSS816NWH6327XTSA1 | https://ngspice.sourceforge.io/docs/ngspice-html-manual/manual.xhtml#cha_MOSFETs | Package_TO_SOT_SMD:SOT-323_SC-70 | 1
Q2 | S8550 | http://www.unisonic.com.tw/datasheet/S8550.pdf | Package_TO_SOT_SMD:SOT-23-3 | 1
R1,R6,R7 | 100 | ~ | Resistor_SMD:R_0603_1608Metric_Pad0.98x0.95mm_HandSolder | 3
R2,R8,R18 | 5.1k | ~ | Resistor_SMD:R_0603_1608Metric_Pad0.98x0.95mm_HandSolder | 3
R3,R13,R14,R15,R19,R20 | 10k | ~ | Resistor_SMD:R_0603_1608Metric_Pad0.98x0.95mm_HandSolder | 6
R4 | 20k | ~ | Resistor_SMD:R_0603_1608Metric_Pad0.98x0.95mm_HandSolder | 1
R5,R21 | 8.2k | ~ | Resistor_SMD:R_0603_1608Metric_Pad0.98x0.95mm_HandSolder | 2
R9,R22 | 0 | ~ | Resistor_SMD:R_0603_1608Metric_Pad0.98x0.95mm_HandSolder | 2 | DNP
R10,R11,R12,R16,R17 | 0 | ~ | Resistor_SMD:R_0603_1608Metric_Pad0.98x0.95mm_HandSolder | 5
RV1,RV2,RV3,RV4 | 100k Trim Pot | ~ | Potentiometer_SMD:Potentiometer_Bourns_TC33X_Vertical | 4
SW2,SW3 | PTS810 SJM 250 SMTR LFS | PTS810 SJM 250 SMTR LFS | PTS810SJM250SMTR LFS:PTS810_CNK | 2
SW4 | JS102011SAQN | ~ | Button_Switch_SMD:SW_SPDT_CK_JS102011SAQN | 1
TP1,TP2,TP_ADC2,TP_AND1,TP_BOOT1,TP_LCELL_VCC1,TP_PU_EN1 | TestPoint | ~ | -- mixed values -- | 7
U1 | HX711 | https://web.archive.org/web/20220615044707/https://akizukidenshi.com/download/ds/avia/hx711.pdf | Package_SO:SOP-16_3.9x9.9mm_P1.27mm | 1
U2 | 74LS21 | http://www.ti.com/lit/gpn/sn74LS21 | Package_SO:SOIC-14_3.9x8.7mm_P1.27mm | 1
U3,U6 | AZ1117CH-3.3 | https://www.diodes.com/assets/Datasheets/AZ1117.pdf | Package_TO_SOT_SMD:SOT-223-3_TabPin2 | 2
U4 | MCP6004 | http://ww1.microchip.com/downloads/en/DeviceDoc/21733j.pdf | Package_SO:SOIC-14_3.9x8.7mm_P1.27mm | 1
U5 | ESP32-S3-WROOM-1-N16R8 | https://www.espressif.com/sites/default/files/documentation/esp32-s3-wroom-1_wroom-1u_datasheet_en.pdf | PCM_Espressif:ESP32-S3-WROOM-1 | 1

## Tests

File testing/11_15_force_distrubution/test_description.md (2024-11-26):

##This test was intended to observe variation in force reading from the load cell when force is applied at various points on a board attached to the load cell.
* A bottle of rice vinegar was weighed with a kitchen scale as a control.
* The rice vinegar weights 773 g

Maximium variation found in "back" position (indicated in photos) of 765g.
Compared with control of 773, difference of 8g. This shows a maximum error of 0.0176lb.

Conclusion: This is a small amount of error, but can be reduced by reducing size of platform. A more rigid platform will also be used in final design, reducing this error further.

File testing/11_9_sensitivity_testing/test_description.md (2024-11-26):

##This test was intended to observe changes in force sensor sentivity and voltage output, given variations in series resistance.

* Using a 100k potentiometer, Vout is measured from 2V to 5V at min and max range of potentiometer. It just works.

Conclusion: Just add some pots to the board and do some more testing.

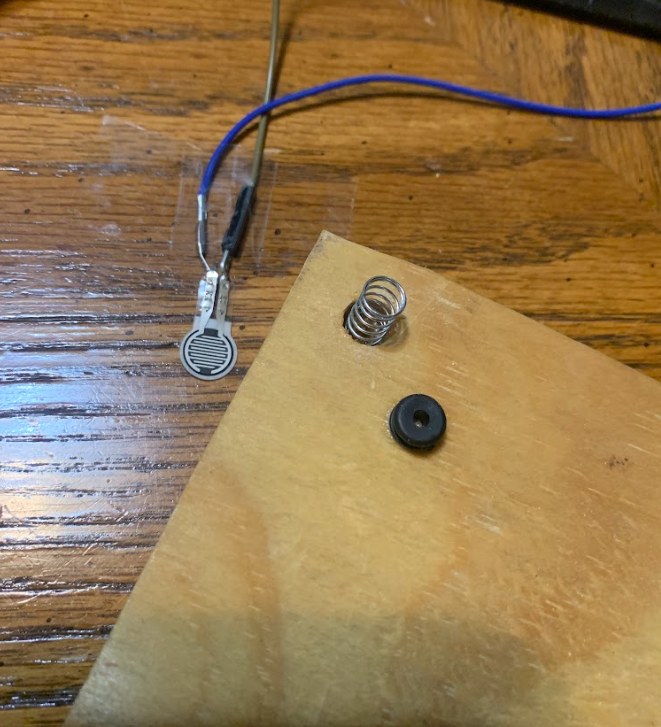
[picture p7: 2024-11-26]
testing/11_9_sensitivity_testing/sensor.png

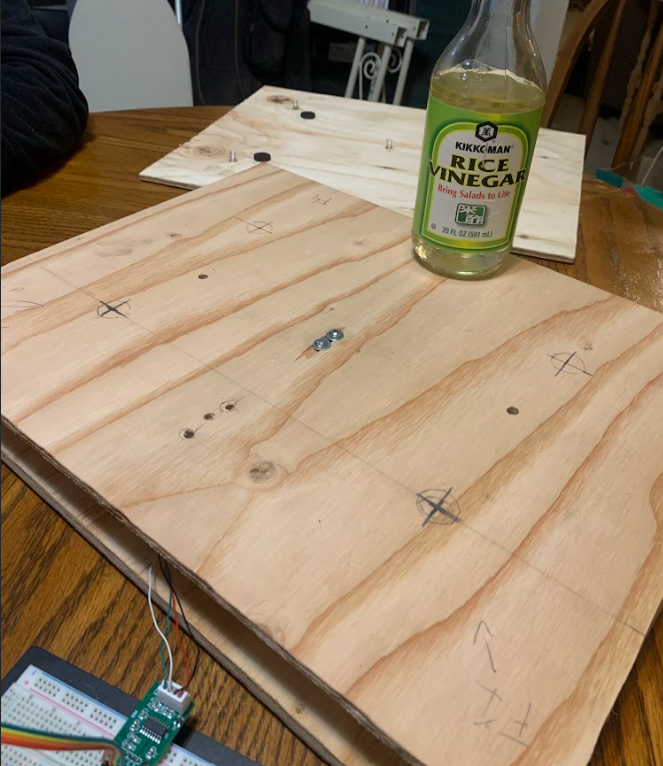
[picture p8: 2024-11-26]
testing/11_15_force_distrubution/back_board.png

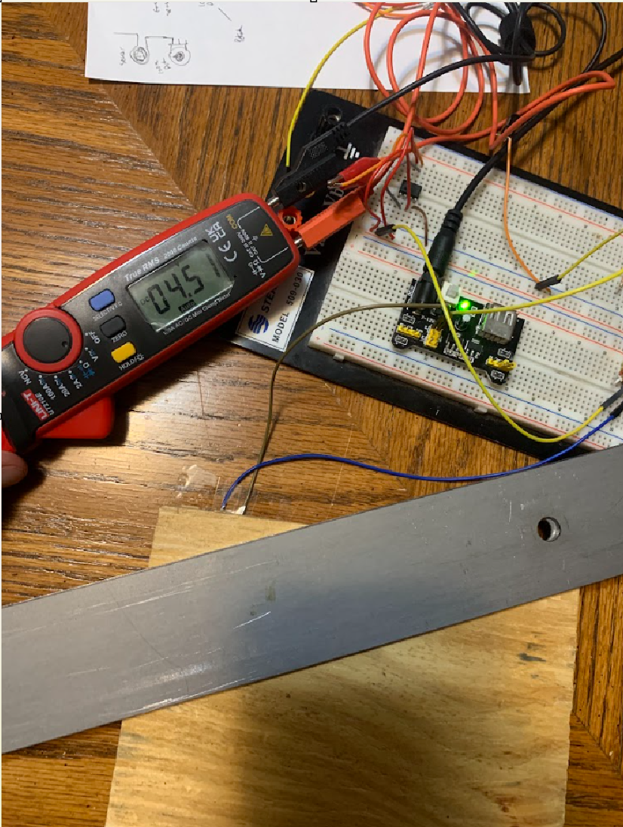
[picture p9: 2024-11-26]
testing/11_9_sensitivity_testing/force_applied.png

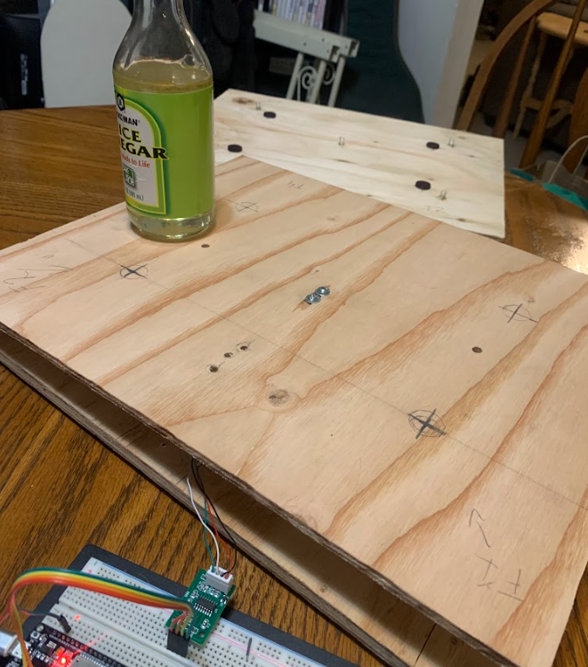
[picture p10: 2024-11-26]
testing/11_15_force_distrubution/left_board.png

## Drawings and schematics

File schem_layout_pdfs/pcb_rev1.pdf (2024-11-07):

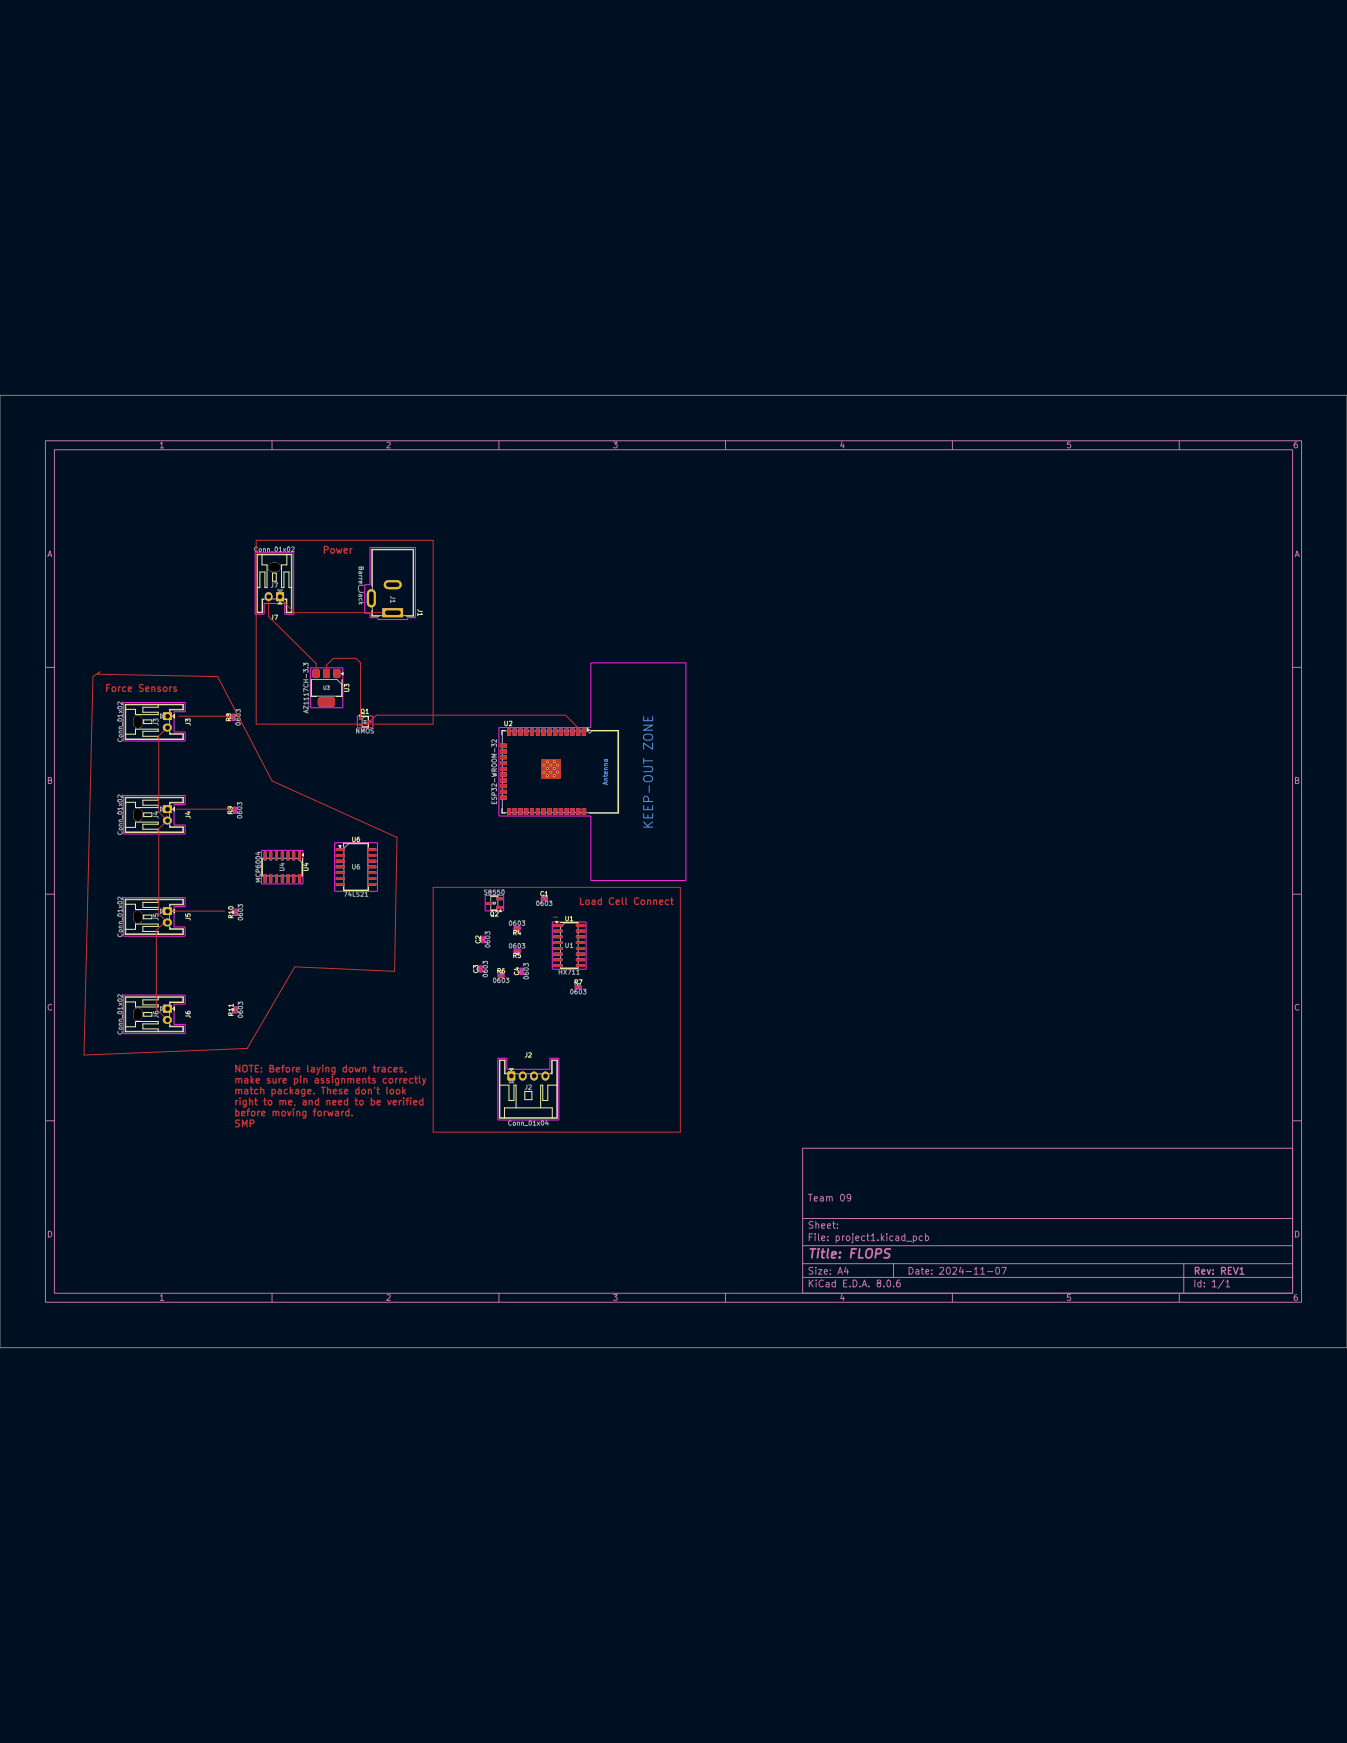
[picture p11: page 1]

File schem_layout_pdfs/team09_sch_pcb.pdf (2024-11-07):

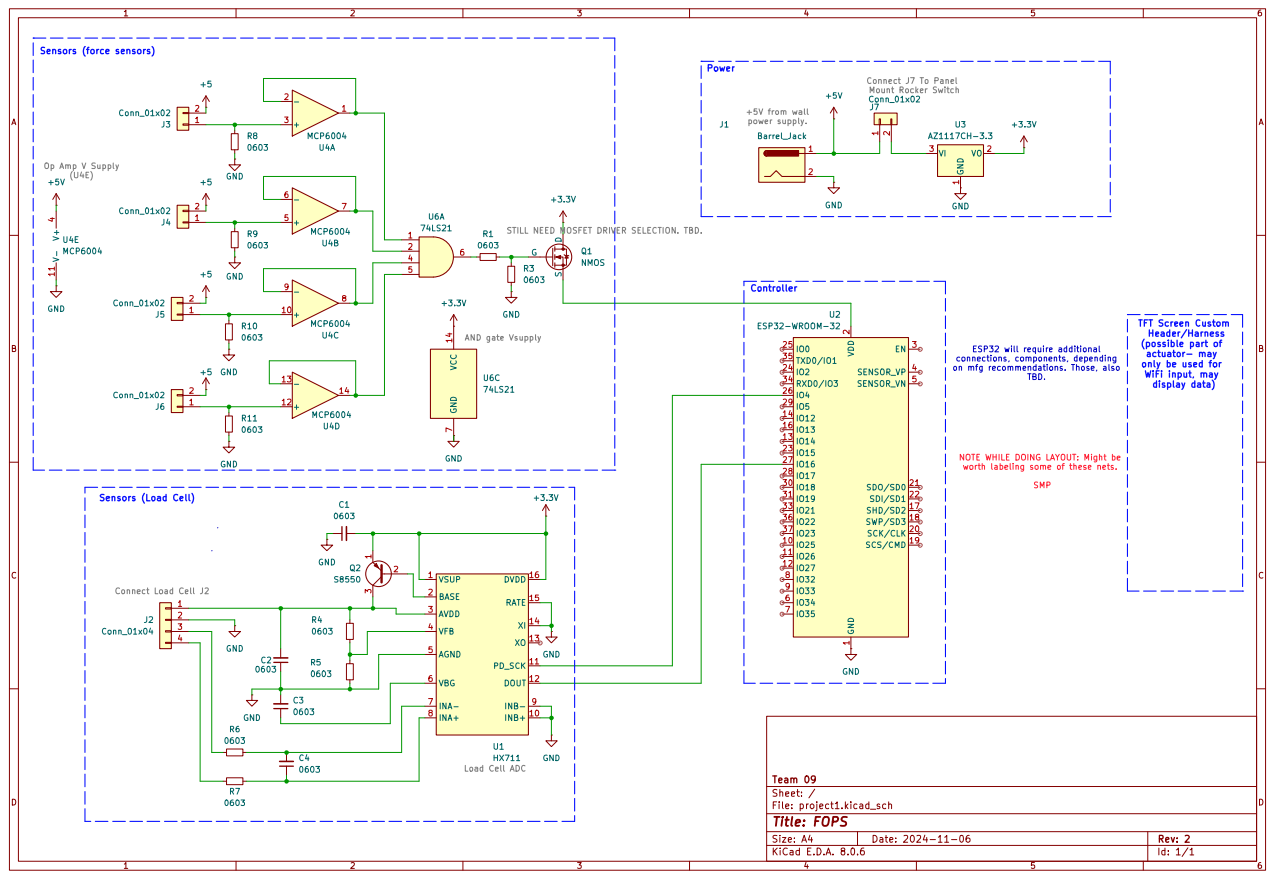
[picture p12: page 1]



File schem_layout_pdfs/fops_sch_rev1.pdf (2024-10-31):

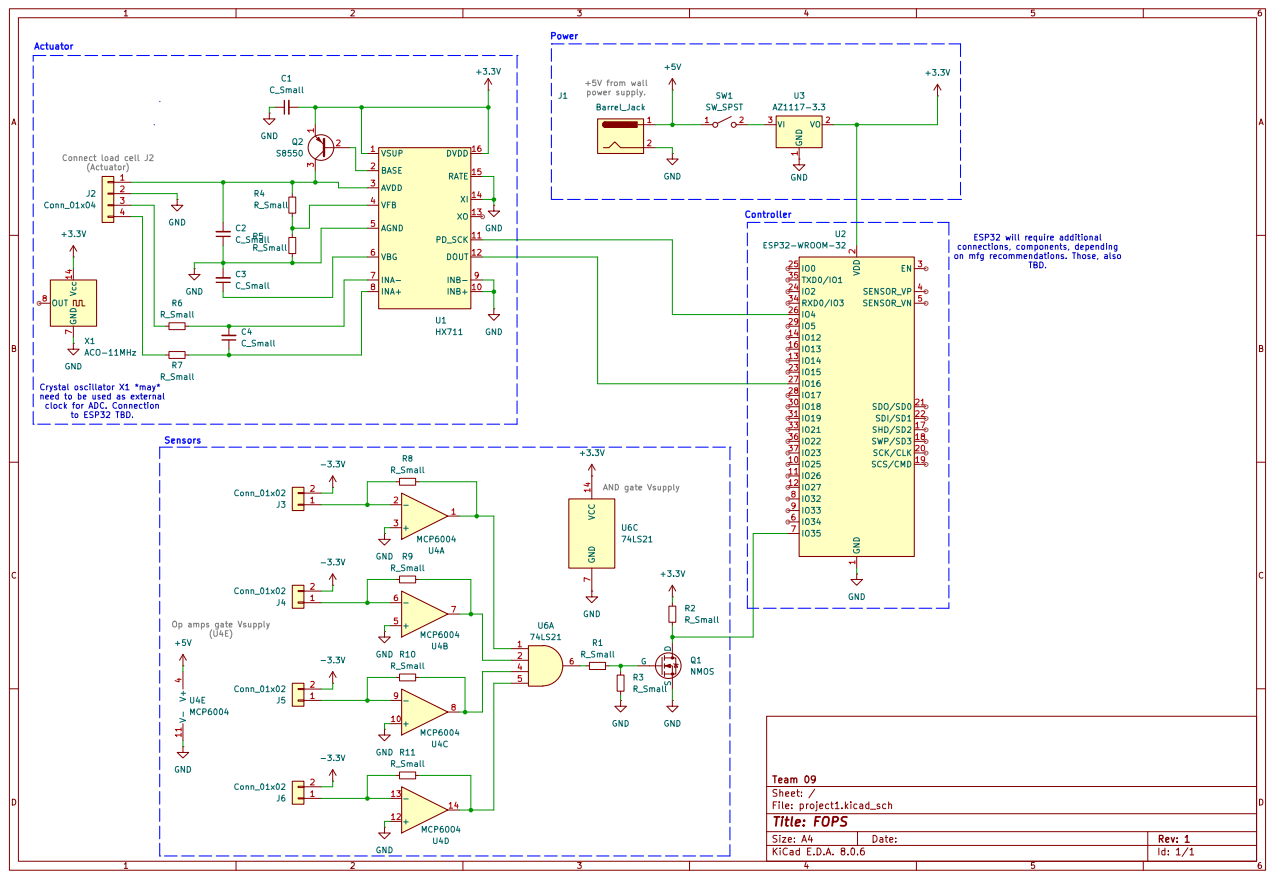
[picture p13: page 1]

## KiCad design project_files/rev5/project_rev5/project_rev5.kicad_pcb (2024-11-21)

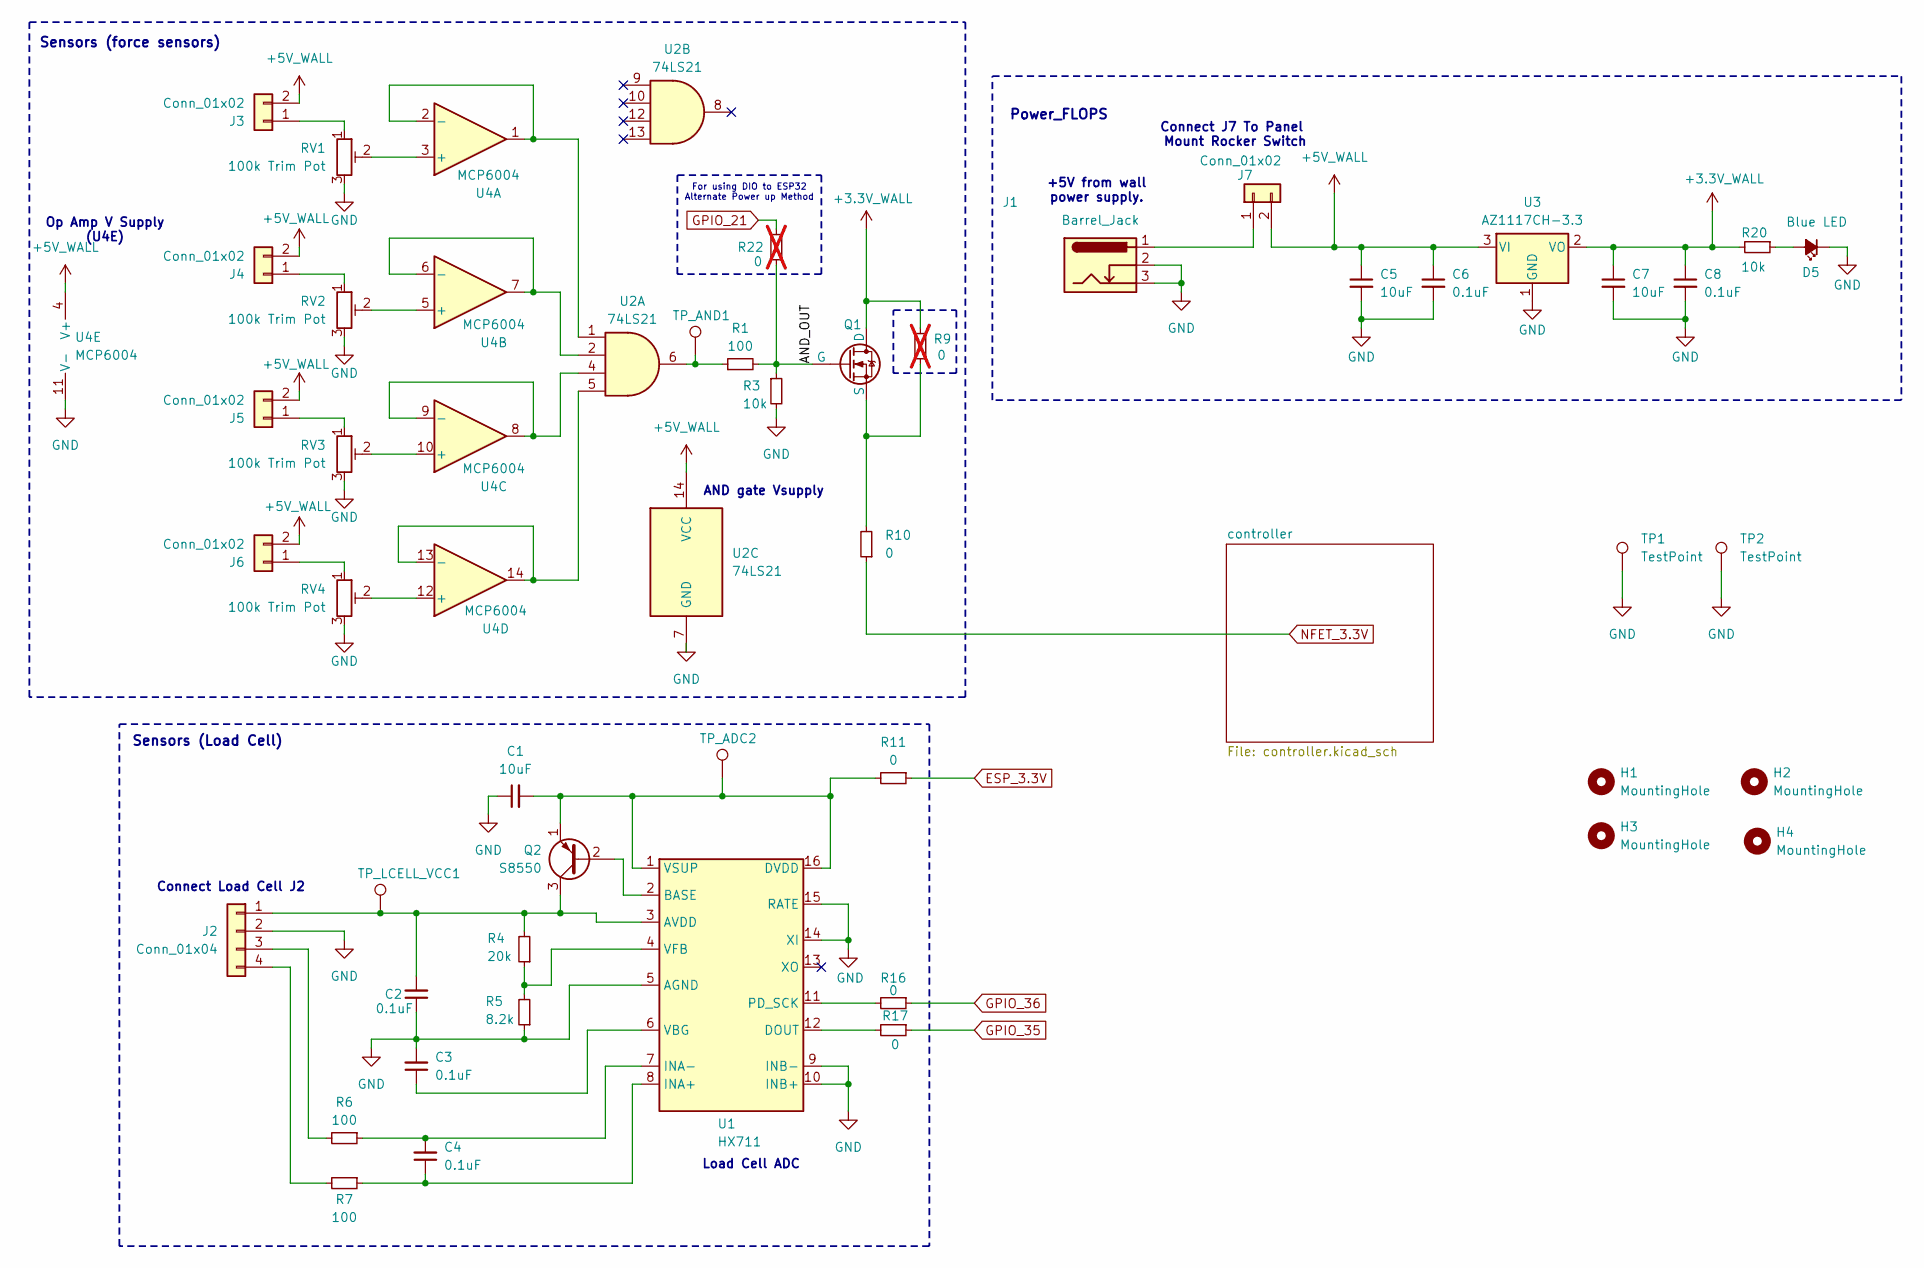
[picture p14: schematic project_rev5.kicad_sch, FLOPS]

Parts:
C1, C5, C7: 10uF; C_0603_1608Metric_Pad1.08x0.95mm_HandSolder
C2, C3, C4, C6, C8: 0.1uF; C_0603_1608Metric_Pad1.08x0.95mm_HandSolder
D5: 150060BS75000; LED_0603_1608Metric
H1, H2, H3, H4: MountingHole; MountingHole_3.2mm_M3_Pad
J1: Barrel_Jack; BarrelJack_Kycon_KLDX-0202-xC_Horizontal
J2: Conn_01x04; JST_XA_S04B-XASK-1N-BN_1x04_P2.50mm_Horizontal
J3, J4, J5, J6, J7: Conn_01x02; JST_XA_S02B-XASK-1N-BN_1x02_P2.50mm_Horizontal
Q1: BSS816NWH6327XTSA1; SOT-323_SC-70
Q2: S8550; SOT-23-3
R1, R6, R7: 100; R_0603_1608Metric_Pad0.98x0.95mm_HandSolder
R3, R20: 10k; R_0603_1608Metric_Pad0.98x0.95mm_HandSolder
R4: 20k; R_0603_1608Metric_Pad0.98x0.95mm_HandSolder
R5: 8.2k; R_0603_1608Metric_Pad0.98x0.95mm_HandSolder
R9, R22: 0; R_0603_1608Metric_Pad0.98x0.95mm_HandSolder; not fitted
R10, R11, R16, R17: 0; R_0603_1608Metric_Pad0.98x0.95mm_HandSolder
RV1, RV2, RV3, RV4: 100k Trim Pot; Potentiometer_Bourns_TC33X_Vertical
TP1, TP2: TestPoint; TestPoint_Keystone_5015_Micro-Minature
TP_ADC2: TestPoint; TestPoint_THTPad_D1.5mm_Drill0.7mm
TP_AND1: TestPoint; TestPoint_THTPad_D1.5mm_Drill0.7mm
TP_LCELL_VCC1: TestPoint; TestPoint_THTPad_D1.5mm_Drill0.7mm
U1: HX711; SOP-16_3.9x9.9mm_P1.27mm
U2: 74LS21; SOIC-14_3.9x8.7mm_P1.27mm
U3: AZ1117CH-3.3; SOT-223-3_TabPin2
U4: MCP6004; SOIC-14_3.9x8.7mm_P1.27mm

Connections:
+3.3V_WALL: C7.1, C8.1, Q1.1 (D), R9.2, R20.2, U3.2 (VO)
+5V_WALL: C5.1, C6.1, J3.2, J4.2, J5.2, J6.2, J7.2, U2.14 (VCC), U3.3 (VI), U4.4 (V+)
/AND_OUT: Q1.2 (G), R1.2, R3.1, R22.1
ESP_3.3V: R11.1; also elsewhere on the board
GND: C1.1, C2.1, C3.2, C5.2, C6.2, C7.2, C8.2, D5.1 (K), J1.2, J1.3, J2.2, R3.2, R5.1, RV1.3, RV2.3, RV3.3, RV4.3, TP1.1, TP2.1, U1.5 (AGND), U1.9 (INB-), U1.10 (INB+), U1.14 (XI), U1.15 (RATE), U2.7 (GND), U3.1 (GND), U4.11 (V-); also elsewhere on the board
GPIO_21: R22.2; also elsewhere on the board
GPIO_35: R17.1; also elsewhere on the board
GPIO_36: R16.1; also elsewhere on the board
NFET_3.3V: R10.1; also elsewhere on the board
unnamed: D5.2 (A), R20.1
unnamed: C2.2, J2.1, Q2.3 (C), R4.2, TP_LCELL_VCC1.1, U1.3 (AVDD)
unnamed: J2.3, R6.2
unnamed: J2.4, R7.2
unnamed: J3.1, RV1.1
unnamed: J4.1, RV2.1
unnamed: J5.1, RV3.1
unnamed: J6.1, RV4.1
unnamed: J1.1, J7.1
unnamed: Q1.3 (S), R9.1, R10.2
unnamed: Q2.2 (B), U1.2 (BASE)
unnamed: C1.2, Q2.1 (E), R11.2, TP_ADC2.1, U1.1 (VSUP), U1.16 (DVDD)
unnamed: R1.1, TP_AND1.1, U2.6
unnamed: R17.2, U1.12 (DOUT)
unnamed: C4.1, R7.1, U1.8 (INA+)
unnamed: C4.2, R6.1, U1.7 (INA-)
unnamed: R16.2, U1.11 (PD_SCK)
unnamed: C3.1, U1.6 (VBG)
unnamed: R4.1, R5.2, U1.4 (VFB)
unnamed: RV1.2, U4.3 (+)
unnamed: U2.1, U4.1, U4.2 (-)
unnamed: RV2.2, U4.5 (+)
unnamed: U2.2, U4.6 (-), U4.7
unnamed: RV3.2, U4.10 (+)
unnamed: U2.4, U4.8, U4.9 (-)
unnamed: RV4.2, U4.12 (+)
unnamed: U2.5, U4.13 (-), U4.14

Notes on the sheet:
Connect J7 To Panel Mount Rocker Switch
Power_FLOPS
+5V from wall power supply.
Op Amp V Supply (U4E)
Sensors (Load Cell)
Load Cell ADC
For using DIO to ESP32 Alternate Power up Method
Sensors (force sensors)
Connect Load Cell J2
AND gate Vsupply

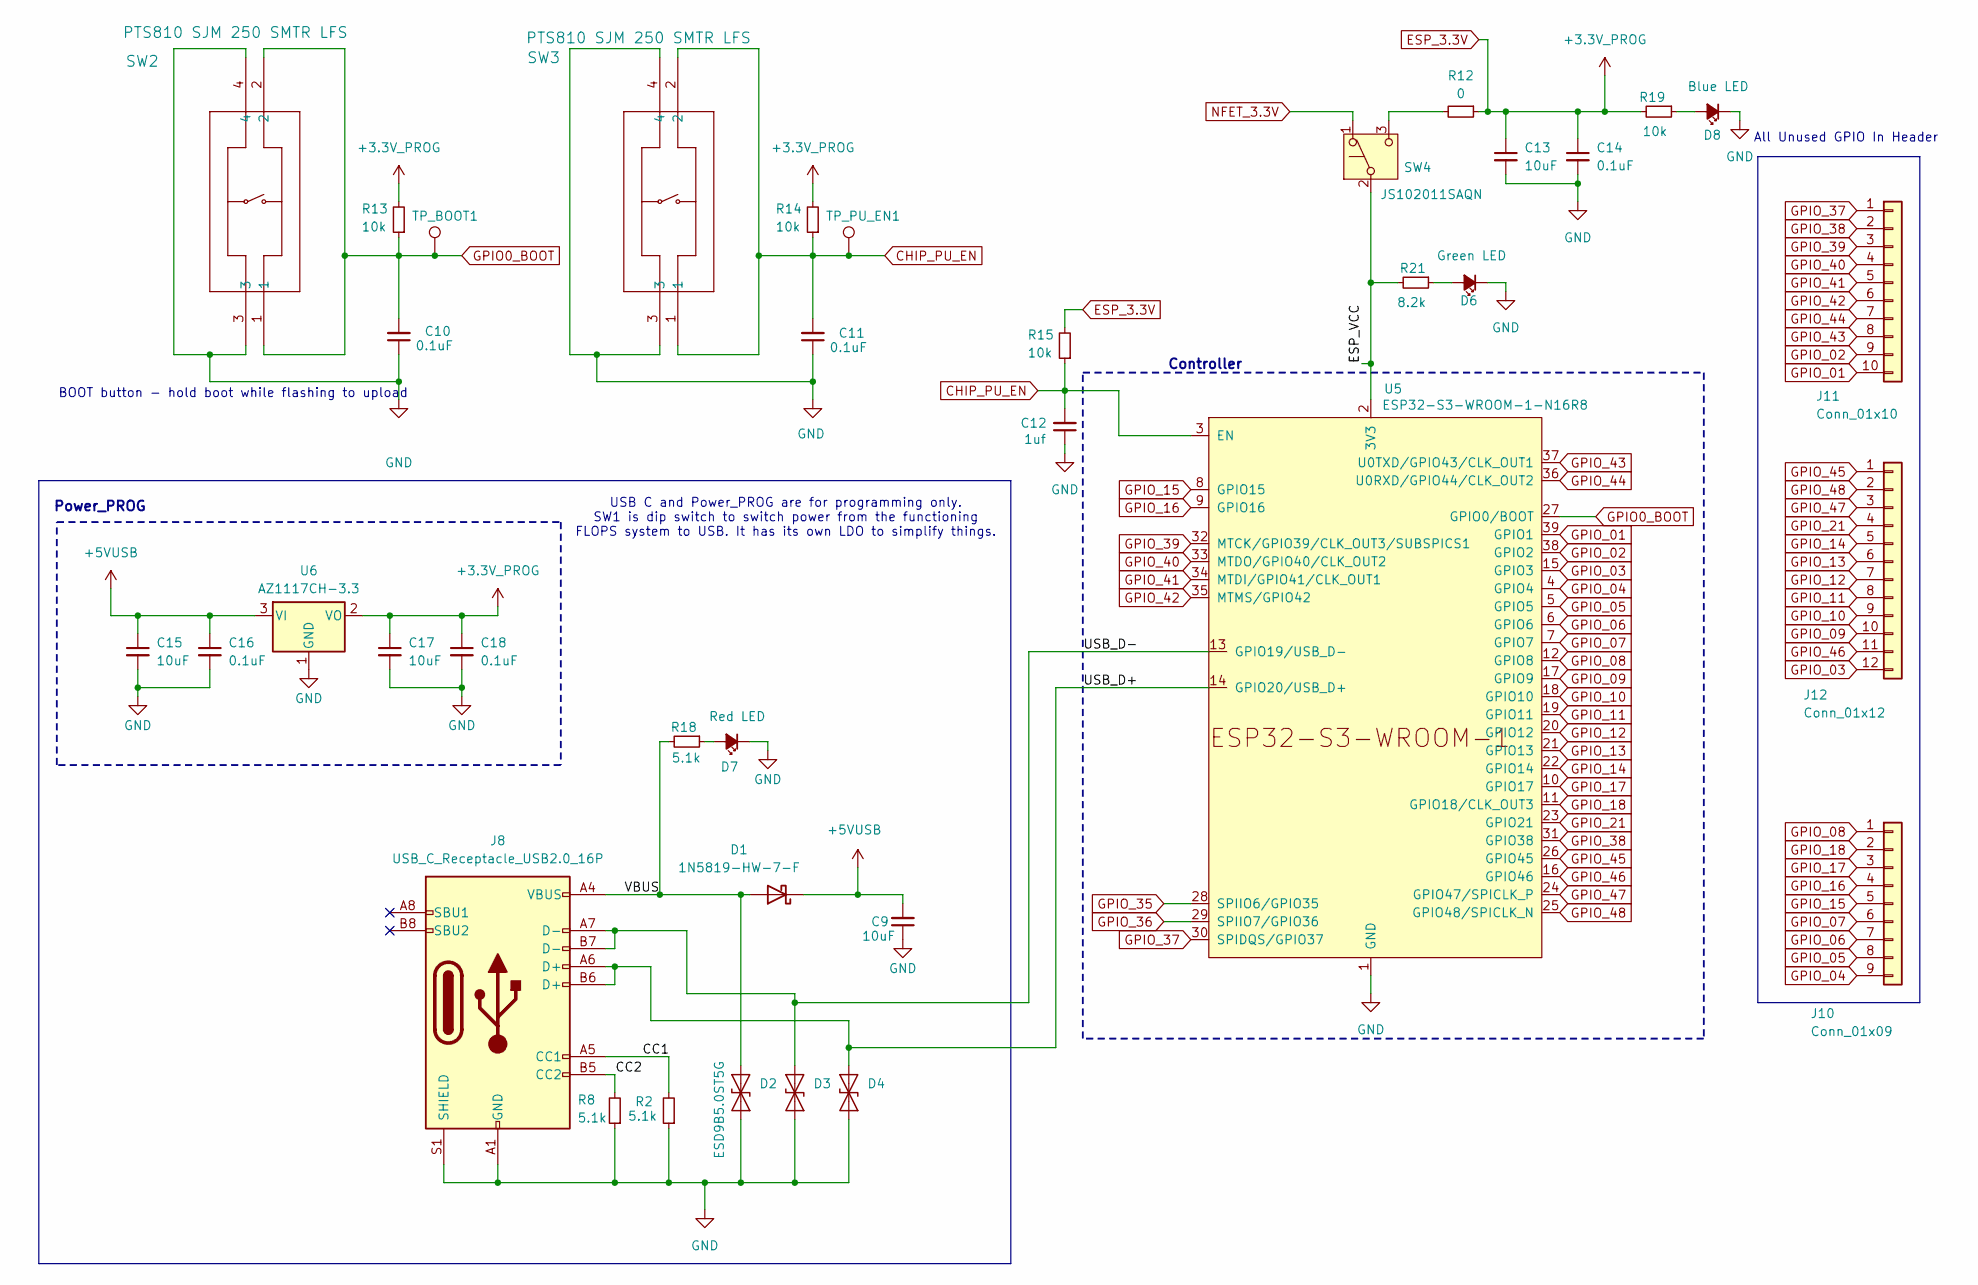
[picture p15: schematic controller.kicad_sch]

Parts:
C9, C13, C15, C17: 10uF; C_0603_1608Metric_Pad1.08x0.95mm_HandSolder
C10, C11, C14, C16, C18: 0.1uF; C_0603_1608Metric_Pad1.08x0.95mm_HandSolder
C12: 1uf; C_0603_1608Metric_Pad1.08x0.95mm_HandSolder
D1: 1N5819-HW-7-F; D_SOD-123
D2, D3, D4: ESD9B5.0ST5G; D_SOD-923
D6, D8: 150060BS75000; LED_0603_1608Metric
D7: 150060RS75000; LED_0603_1608Metric
J8: USB_C_Receptacle_USB2.0_16P; USB_C_Receptacle_GCT_USB4105-xx-A_16P_TopMnt_Horizontal
J10: Conn_01x09; PinHeader_1x09_P2.54mm_Vertical
J11: Conn_01x10; PinHeader_1x10_P2.54mm_Vertical
J12: Conn_01x12; PinHeader_1x12_P2.54mm_Vertical
R2, R8, R18: 5.1k; R_0603_1608Metric_Pad0.98x0.95mm_HandSolder
R12: 0; R_0603_1608Metric_Pad0.98x0.95mm_HandSolder
R13, R14, R15, R19: 10k; R_0603_1608Metric_Pad0.98x0.95mm_HandSolder
R21: 8.2k; R_0603_1608Metric_Pad0.98x0.95mm_HandSolder
SW2, SW3: PTS810 SJM 250 SMTR LFS; PTS810_CNK
SW4: JS102011SAQN; SW_SPDT_CK_JS102011SAQN
TP_BOOT1: TestPoint; TestPoint_THTPad_D1.5mm_Drill0.7mm
TP_PU_EN1: TestPoint; TestPoint_THTPad_D1.5mm_Drill0.7mm
U5: ESP32-S3-WROOM-1-N16R8; ESP32-S3-WROOM-1
U6: AZ1117CH-3.3; SOT-223-3_TabPin2

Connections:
+5VUSB: C9.2, C15.1, C16.1, D1.1 (K), U6.3 (VI)
/controller/CC1: J8.A5 (CC1), R2.2
/controller/CC2: J8.B5 (CC2), R8.2
/controller/ESP_VCC: R21.2, SW4.2 (B), U5.2 (3V3)
/controller/USB_D+: D4.1 (A1), J8.A6 (D+), J8.B6 (D+), U5.14 (GPIO20/USB_D+)
/controller/USB_D-: D3.1 (A1), J8.A7 (D-), J8.B7 (D-), U5.13 (GPIO19/USB_D-)
/controller/VBUS: D1.2 (A), D2.1 (A1), J8.A4 (VBUS), J8.A9 (VBUS), J8.B4 (VBUS), J8.B9 (VBUS), R18.2
CHIP_PU_EN: C11.2, C12.2, R14.1, R15.1, SW3.1, SW3.2, TP_PU_EN1.1, U5.3 (EN)
ESP_3.3V: C13.1, C14.1, C17.1, C18.1, R12.1, R13.2, R14.2, R15.2, R19.2, U6.2 (VO); also elsewhere on the board
GND: C9.1, C10.1, C11.1, C12.1, C13.2, C14.2, C15.2, C16.2, C17.2, C18.2, D2.2 (A2), D3.2 (A2), D4.2 (A2), D6.1 (K), D7.1 (K), D8.1 (K), J8.A1 (GND), J8.A12 (GND), J8.B1 (GND), J8.B12 (GND), J8.S1 (SHIELD), R2.1, R8.1, SW2.3, SW2.4, SW3.3, SW3.4, U5.1 (GND), U5.40 (GND), U5.41 (GND), U6.1 (GND); also elsewhere on the board
GPIO0_BOOT: C10.2, R13.1, SW2.1, SW2.2, TP_BOOT1.1, U5.27 (GPIO0/BOOT)
GPIO_01: J11.10, U5.39 (GPIO1)
GPIO_02: J11.9, U5.38 (GPIO2)
GPIO_03: J12.12, U5.15 (GPIO3)
GPIO_04: J10.9, U5.4 (GPIO4)
GPIO_05: J10.8, U5.5 (GPIO5)
GPIO_06: J10.7, U5.6 (GPIO6)
GPIO_07: J10.6, U5.7 (GPIO7)
GPIO_08: J10.1, U5.12 (GPIO8)
GPIO_09: J12.10, U5.17 (GPIO9)
GPIO_10: J12.9, U5.18 (GPIO10)
GPIO_11: J12.8, U5.19 (GPIO11)
GPIO_12: J12.7, U5.20 (GPIO12)
GPIO_13: J12.6, U5.21 (GPIO13)
GPIO_14: J12.5, U5.22 (GPIO14)
GPIO_15: J10.5, U5.8 (GPIO15)
GPIO_16: J10.4, U5.9 (GPIO16)
GPIO_17: J10.3, U5.10 (GPIO17)
GPIO_18: J10.2, U5.11 (GPIO18/CLK_OUT3)
GPIO_21: J12.4, U5.23 (GPIO21); also elsewhere on the board
GPIO_35: U5.28 (SPIIO6/GPIO35); also elsewhere on the board
GPIO_36: U5.29 (SPIIO7/GPIO36); also elsewhere on the board
GPIO_37: J11.1, U5.30 (SPIDQS/GPIO37)
GPIO_38: J11.2, U5.31 (GPIO38)
GPIO_39: J11.3, U5.32 (MTCK/GPIO39/CLK_OUT3/SUBSPICS1)
GPIO_40: J11.4, U5.33 (MTDO/GPIO40/CLK_OUT2)
GPIO_41: J11.5, U5.34 (MTDI/GPIO41/CLK_OUT1)
GPIO_42: J11.6, U5.35 (MTMS/GPIO42)
GPIO_43: J11.8, U5.37 (U0TXD/GPIO43/CLK_OUT1)
GPIO_44: J11.7, U5.36 (U0RXD/GPIO44/CLK_OUT2)
GPIO_45: J12.1, U5.26 (GPIO45)
GPIO_46: J12.11, U5.16 (GPIO46)
GPIO_47: J12.3, U5.24 (GPIO47/SPICLK_P)
GPIO_48: J12.2, U5.25 (GPIO48/SPICLK_N)
NFET_3.3V: SW4.1 (A); also elsewhere on the board
unnamed: D6.2 (A), R21.1
unnamed: D7.2 (A), R18.1
unnamed: D8.2 (A), R19.1
unnamed: R12.2, SW4.3 (C)

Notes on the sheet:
Controller
All Unused GPIO In Header
USB C and Power_PROG are for programming only. SW1 is dip switch to switch power from the functioning FLOPS system to USB. It has its own LDO to simplify things.
BOOT button - hold boot while flashing to upload
Power_PROG

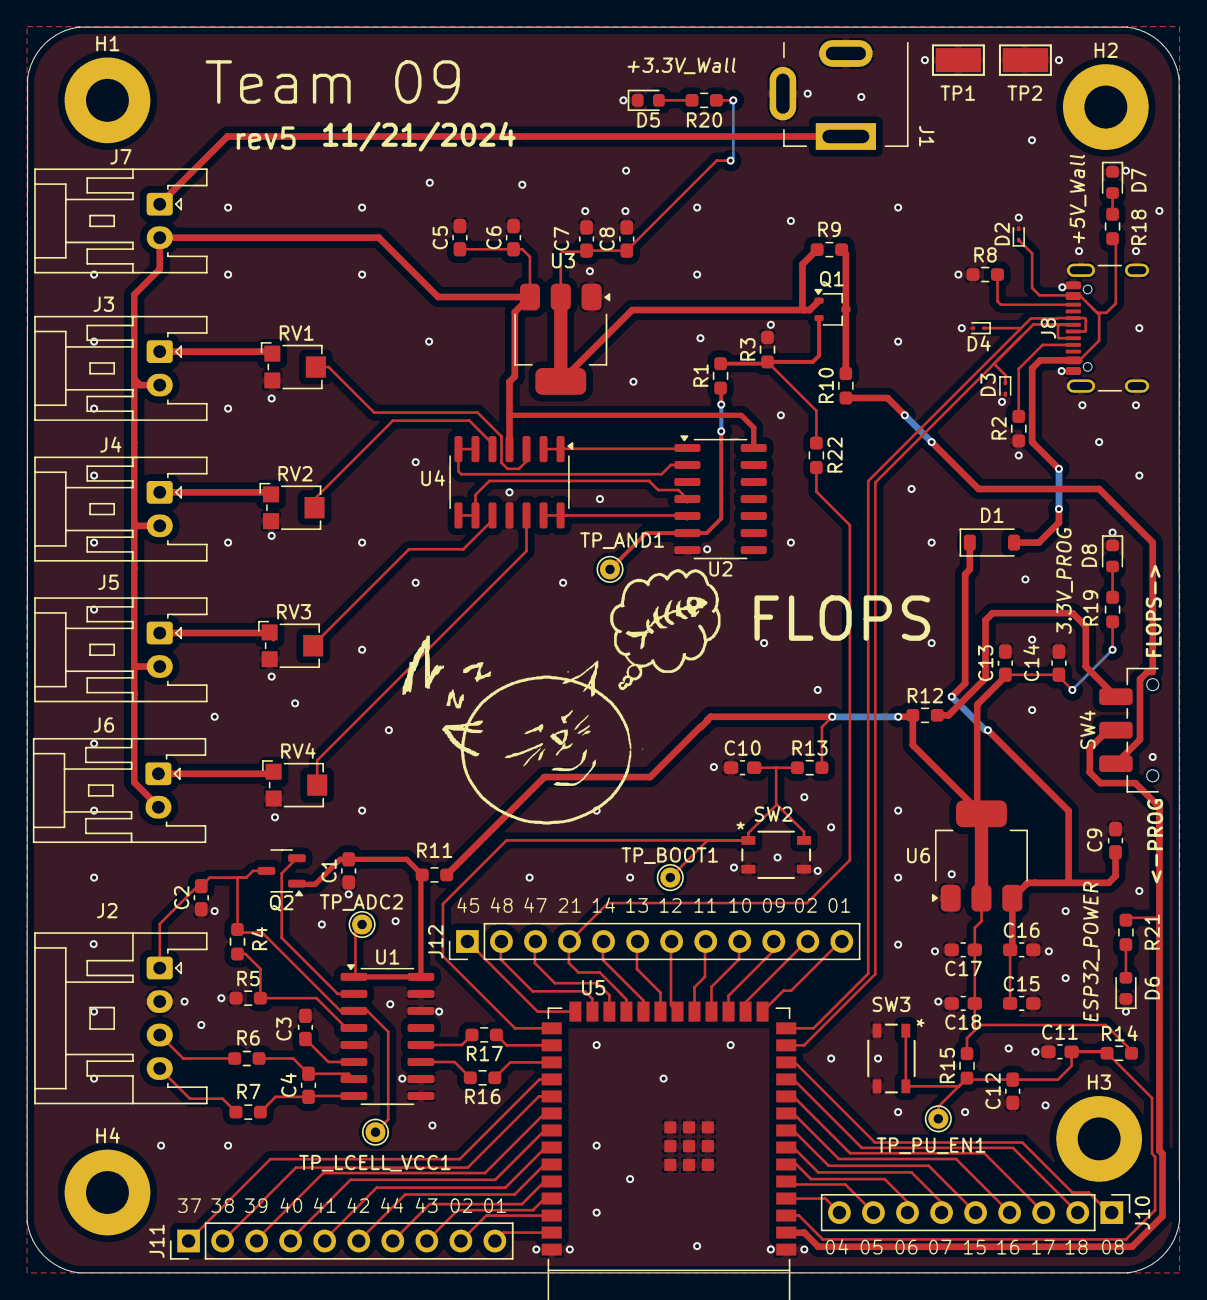
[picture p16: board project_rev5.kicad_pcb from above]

Board: 2 copper layers, 86.0 x 93.0 mm, 85 parts (0 on the bottom side), 79 nets.

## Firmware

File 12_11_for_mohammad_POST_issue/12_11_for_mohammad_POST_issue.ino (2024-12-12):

#include <Arduino.h>
#include "HX711.h"
#include "soc/rtc.h"
#include <WiFi.h>
#include <HTTPClient.h>
#include "time.h"

#define PIN_INTERRUPT 21
#define MAX_DATA_PER_DAY 100
char* WIFI_SSID = "Mohammad";
char* password = "Hamoor221";
char* serverName = "http://helloflops.com/submit";

unsigned long timerDelay = 5000;

// HX711 circuit wiring
const int LOADCELL_DOUT_PIN = 35;
const int LOADCELL_SCK_PIN = 36;

HX711 scale;

double weightArray[MAX_DATA_PER_DAY];  // Array to store weight measurements
int weightIndex = 0;  // To track number of stored weights
unsigned long lastTime = 0;

const int interruptPin = PIN_INTERRUPT;

// Helper function to get zero-padded strings for date/time components
String twoDigitString(int value) {
  if (value < 10) {
    return "0" + String(value);
  } else {
    return String(value);
  }
}

void sendWeight(double weight, String dateStr) {
  if (WiFi.status() == WL_CONNECTED) {
    WiFiClient client;
    HTTPClient http;
    http.begin(client, serverName);

    String weightStr = String(weight, DEC);
    // Data in the format "weight=...&date=YYYY-MM-DD HH:MM"
    String dataToSend = "weight=" + weightStr + "&date=" + dateStr;

    http.addHeader("Content-Type", "application/x-www-form-urlencoded");
    int responseCode = http.POST(dataToSend);

    Serial.print("Code Returned: ");
    Serial.println(responseCode);

    http.end();
  } else {
    Serial.println("WiFi Disconnected");
  }
}

void calculateAndSendAverage(String dateStr) {
  double totalWeight = 0;
  for (int i = 0; i < weightIndex; i++) {
    totalWeight += weightArray[i];
  }
  double averageWeight = totalWeight / weightIndex;

  // Reset the array for the next set of readings
  weightIndex = 0;

  sendWeight(averageWeight, dateStr);
}

void setup() {
  Serial.begin(115200);

  rtc_cpu_freq_config_t config;
  rtc_clk_cpu_freq_get_config(&config);
  rtc_clk_cpu_freq_set_config_fast(&config);
  
  scale.begin(LOADCELL_DOUT_PIN, LOADCELL_SCK_PIN);
  scale.set_scale(104.84);
  scale.tare();
  
  pinMode(interruptPin, INPUT_PULLDOWN);

  // Initialize WiFi
  WiFi.begin(WIFI_SSID, password);
  while (WiFi.status() != WL_CONNECTED) {
    delay(500);
    Serial.print("Connecting...\n");
  }
  Serial.print("Connected. IP Address: ");
  Serial.println(WiFi.localIP());

  // Initialize time
  configTime(0, 0, "pool.ntp.org"); // Synchronize time using NTP
}

void loop() {
  scale.power_up();
  if (digitalRead(interruptPin) == HIGH) {
    // Get current time
    time_t now;
    struct tm timeinfo;
    if (!getLocalTime(&timeinfo)) {
      Serial.println("Failed to obtain time");
      return;
    }

    int currentHour = timeinfo.tm_hour;
    int currentMinute = timeinfo.tm_min;

    // Check if the time is within 30 minutes of midnight (00:00)
    bool isNearMidnight = 1;
    //(currentHour == 23 && currentMinute >= 30) || (currentHour == 0 && currentMinute == 0);

    // Build the date string with zero-padding
    String yearStr = String(timeinfo.tm_year + 1900);
    String monthStr = twoDigitString(timeinfo.tm_mon + 1);
    String dayStr = twoDigitString(timeinfo.tm_mday);
    String hourStr = twoDigitString(timeinfo.tm_hour);
    String minuteStr = twoDigitString(timeinfo.tm_min);

    String dateStr = yearStr + "-" + monthStr + "-" + dayStr + " " + hourStr + ":" + minuteStr;

    scale.power_up();

    double weight = scale.get_units();

    if (isNearMidnight) {
      if (weightIndex == 0) {
        Serial.println("Weight index is zero, sending data");
        // If the array is empty, send the current weight
        sendWeight(weight, dateStr);
      } else {
        // If there's data in the array, calculate and send the average weight
        calculateAndSendAverage(dateStr);
      }
    } else {
      // Store weight in the array if not within 30 minutes of midnight
      Serial.println("In weight array loop");
      if (weightIndex < MAX_DATA_PER_DAY) {
        weightArray[weightIndex] = weight;
        weightIndex++;
      } else {
        // If the array is full, calculate and send average
        calculateAndSendAverage(dateStr);
      }
    }

  }
  // Go back to light sleep after the interrupt is processed (if needed)
  // esp_light_sleep_start();
}

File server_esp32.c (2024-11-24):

#include <Arduino.h>
#include "HX711.h"
#include "soc/rtc.h"
#include <WiFi.h>
#include <HTTPClient.h>
#include "time.h"

char* WIFI_SSID = "SSID";
char* password = "PASSWORD";

char* serverName = "TO-DO";

unsigned long timerDelay = 5000;

// HX711 circuit wiring
const int LOADCELL_DOUT_PIN = 16;
const int LOADCELL_SCK_PIN = 4;

HX711 scale;

void setup() {
  Serial.begin(115200);
  rtc_cpu_freq_config_t config;
  rtc_clk_cpu_freq_get_config(&config);
  //rtc_clk_cpu_freq_to_config(RTC_CPU_FREQ_80M, &config);
  rtc_clk_cpu_freq_set_config_fast(&config);
  scale.begin(LOADCELL_DOUT_PIN, LOADCELL_SCK_PIN);
  
  struct tm local_time;
  
  scale.set_scale(103.84); //value determined from calibration procedure
  scale.tare();               // reset the scale to 0
  
   WiFi.begin(WIFI_SSID, password);
  while(WiFi.status() != WL_CONNECTED) {
    delay(500);
    Serial.print("Connecting...\n");
  }
  Serial.print("Connected. IP Address: ");
  Serial.println(WiFi.localIP());
}
void loop() {
	if ((millis() - lastTime) > timerDelay) {
    //Check WiFi connection status
    if(WiFi.status()== WL_CONNECTED){
      WiFiClient client;
      HTTPClient http;

      http.begin(client, serverName);
	  scale.power_up();
	  
		if (scale.is_ready()) {
			double weight_as_number = scale.get_units();
			string weight = String(weight_as_number, DEC);
			
			// Specify content-type header
			http.addHeader("Content-Type", "application/x-www-form-urlencoded");
			// Data to send with HTTP POST
			String Data_to_send = String("weight=" + weight + "&day=30"; //example format
			// Send HTTP POST request
			int ResponseCode = http.POST(Data_to_send);
		 
		
			Serial.print("Code Returned: ");
			Serial.println(ResponseCode);

			// Free resources
			http.end();
			scale.power_down();
		}
		else 
		{
			Serial.println("HX711 not found.");
		}
	}
	else
	{
		Serial.println("WiFi Disconnected");
    }
	lastTime = millis();
  }
}
  
  

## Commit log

2024-10-31 rev 1 for preliminary schematic) asdf
    [project1.kicad_pcb, project1.kicad_sch]
2024-11-07 committing pcb and some other cache files
2024-11-07 Stu schem update (#23)
    * adding outline for gantt chart update
    * update schematic, added footprints, started layout.
    [project1.kicad_pcb, project1.kicad_sch]
2024-11-07 Stu schem update (#25)
    * a couple changes
    * added breadboard image, video of load cell weighing a la croix and force sensor on o-scope
    * added markdown for brief status report.
    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
2024-11-14 Bom branch (#31)
    * Test run two
    * test run three
    * BOM Updated Progress
    * BOM Update
    * BOM Official Rough Draft Update
    * BOM Official RD in progress
    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
    [411_BOM_V1.csv, BOM Official for RoughDraft (1).xlsx]
2024-11-14 rev3 schematic and layout (#32)
    * renamed project to current rev. each future rev will get it's own copy in project directory. each rev will not be touched once it has been committed and another rev is being worked on. Added update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
    * added labels to rev3 sch and pcb
    * printed pdf of sch and pcb
    * moved something
    [controller.kicad_sch, project1-B_Cu.gbr, project1-B_Mask.gbr, project1-B_Paste.gbr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]
2024-11-18 making a commit, didn't mean to do it on main but here we are
    [project_rev3.kicad_pcb]
2024-11-18 fucked up a commit, tring to fix
    [controller.kicad_sch, project1-B_Cu.gbr, project1-B_Mask.gbr, project1-B_Paste.gbr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]
2024-11-18 added new project for rev4 and reverted changes for rev3
    [controller.kicad_sch, project1-B_Cu.gbr, project1-B_Mask.gbr, project1-B_Paste.gbr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]
2024-11-20 committing update
    [BOM Official for RoughDraft (1) - Copy.xlsx, controller.kicad_sch, project_rev4.csv, project_rev4.kicad_pcb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]
2024-11-20 final rev4
    [project_rev4.kicad_pcb]
2024-11-20 added updates to rev5!
    [controller.kicad_sch, project_rev5.kicad_pcb, project_rev5.kicad_sch]
2024-11-21 pushing final rev5. may god have mercy.
    [controller.kicad_sch, project_rev5-B_Cu.gbr, project_rev5-B_Mask.gbr, project_rev5-B_Paste.gbr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]
2024-11-21 last adds of pdf of sch and pcb
    [project_rev5.kicad_pcb]
2024-11-23 Initial Prototype of Server In Python
2024-11-23 Basic Server on the ESP32
    Server implementation on ESP32 to send data to web server
2024-11-23 adding basic code for load cell. One for calibrating, one for collecting weight.
2024-11-26 adding some images from previous force sensor and load cell testing.
2024-12-11 final BOM updated
    [BOM Official for RoughDraft (1) - Copy.xlsx, BOM Official for RoughDraft (1).xlsx, BOM_rev1_v1.csv, BOM_rev5_v2.xlsx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]
2024-12-12 seriously, the last one
    [BOM_rev5_v3.xlsx]
